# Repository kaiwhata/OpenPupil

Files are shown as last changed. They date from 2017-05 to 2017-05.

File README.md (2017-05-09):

# OpenPupil
Instuctions for assembly and/or fabrication of our open-source pupilometer.

# Overall system architecture
The overall system design can be seen in our poster presented at ARVO 2017 (https://www.arvo.org/AM/) here.
Our OpenPupil electronic system consists of: a Raspberry Pi 2 B+, with a NoIR camera, two 850nm IR LEDs, a 16 neopixel ring, USB wireless dongle, microSD card . 
Our hardware system consists of: a 3D printed eyepiece, a lazercut enclosure, a Google Cardboard lens
Our software system consists of: a python flask server, a supervisor instance, a C library and program for image collection and processing
A tabulated series of the above components is available below along with prices and purchasing suggestions.
For setup you will also (unless you're proficient with SSH and command line) need an HDMI cable, usb keyboard and mouse.

# Hardware instructions
You can find the lazercut enclosure designs (for 6mm acrylic) here.
You can find the `.stl` file for the 3D printed eyepiece here. Alternatively, if you do not have access to a 3D printer, you can purchase a printed one directly from our Shapeways store here (www.shapeways.com/shops/openpupil).

# RPi Installation instructions
`sudo apt-get install supervisor python-picamera`
`sudo pip install flask`

# Components

| Component     | Cost (USD)         | Purchasing Link |
| ------------- |:-------------:| -----:|
| RPi v2 B+ | $29.95 | https://www.adafruit.com/product/1914 | (a full kit can be purchased here: https://www.adafruit.com/product/2380)
| No IR camera | $29.95 | https://www.adafruit.com/product/387 |
| 850nm IR LEDs * | $0.75ea | https://www.adafruit.com/product/387 |
| Neopixel Ring | $9.95 | https://www.adafruit.com/product/1463 |
| USB Wifi Dongle | $11.95 | https://www.adafruit.com/product/814 |
| microSD card (8 or 16GB)| $14.95 | https://www.adafruit.com/product/1583 |
| 3D printed eyepiece | $ | |
| Google Cardboard v1 lens | $ | |

# Contact Details
This project is currently lead by Dr. Jesse Gale (jesse.gale@gmail.com) with support from Elf Eldridge (kaiwhata@gmail.com) and honours student Shaetrun Pathmanathan.

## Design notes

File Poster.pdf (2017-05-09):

Figure 1 Exploded view of device

# Hardware

# Proposal

# Methods

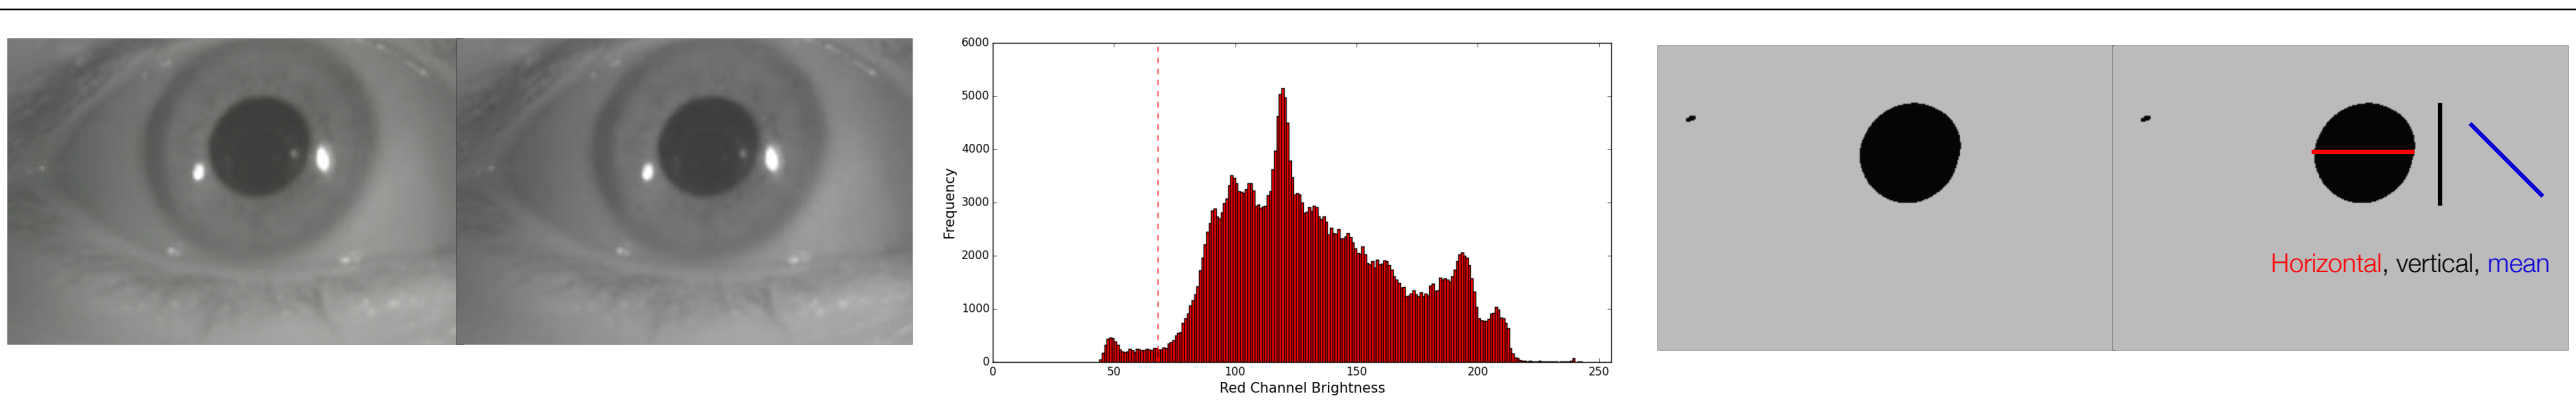
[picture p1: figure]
Horizontal, vertical, mean

## Contacts

To inquire or contribute, or to obtain one of these devices for your own research, please contact us.
Jesse Gale
jesse.gale@gmail.com
+64 21 1272 979
Surgery & Anaesthesia
University of Otago
PO Box 7343
Newtown
Wellington 6242
New Zealand

# Development of an open source pupilometer for testing melanopsin responses

# Dr Jesse Gale¹,2

# , Dr J. Elf Eldridge³

# , Shaetrun Pathmanathan³

# , Kapeteni Polutea³

# , Dr Gideon Gouws³, Prof Simon Fraser⁴

1) Surgery & Anaesthesia, University of Otago, Wellington, New Zealand. 2) Ophthalmology, Capital and Coast District Health Board, Wellington, New Zealand.
3) Engineering and Computer Science, Victoria University, Wellington, New Zealand. 4) Design, Victoria University, Wellington, New Zealand.

We identified the core requirements for versatile pupil testing in a wide range of scenarios, such as anisocoria, refractive surgery planning, testing pupils after head injury, quantifying a relative afferent pupil defect (RAPD), and potentially testing quadrants individually (what could be termed multifocal pupilometry).

These requirements were:
- A close fitting goggle to eliminate ambient light and provide illumination from a large visual angle
- An IR video camera with sufficient optical quality to allow filming of the pupil at high spatial and temporal resolution in both light and dark conditions
- Illumination of high intensity, fine control, all colours, and potentially directional illumination (e.g. testing sectors of the visual field)
- Portability, connecting to a computer or smartphone wirelessly, with a degree of internal data processing

We investigated the cheapest, widely-available components that would meet these requirements.

The design, software, and all early findings were made freely available on an open source directory in the spirit of collaboration.

https://github.com/kaiwhata/openpupil

# Software

Poster # 5090 – B0700

The intrinsically-photosensitive melanopsin-expressing retinal ganglion cells are of interest for several reasons. Quantifying melanopsin function with the post-illumination pupil response (PIPR) is of potential use in clinical research.

Moreover, a cheap and versatile pupilometer may have application in a range of research settings, neurological and ophthalmology practice, and in many primary care settings such as ambulances, emergency departments and family practice.

Standard video pupilometry uses infrared (IR) video of the pupil, lights to stimulate pupil constriction, and software to measure pupil size from the video. The PIPR additionally requires stimulating blue light of high luminance (> 100 mcdm⁻²). Portable pupilometers cost thousands of dollars and do not have capability to test PIPR, while PIPR is usually tested with non-portable electrophysiology equipment costing many tens of thousands of dollars.

Session Number: 489 – Pupil – May 10, 2017

## Can an affordable pupilometer be created using widely available technology, with the required capabilities to test melanopsin function as well as common clinical scenarios?

# Background

The proliferation of cheap components, powerful and versatile microprocessors,

## and 3D printers enables the development of

new clinical and research tools at low cost.

# Conclusions

Optics This biconvex lens functions to bring the camera into focus at a short working distance. These 25 mm plastic lenses of 22 D power are widely available for Google Cardboard virtual reality sets, at a cost < USD $0.40.

Goggle (housing) This functions to exclude ambient light, position the camera at the correct distance in front of the eye, and diffuse incident light to illuminate the whole field. It must be comfortable, ergonomic (fitting most orbits), and hygienic (easy to clean).

We have tested a range of designs and 3D printing materials. Further prototyping continues with flexible, cleanable materials that can diffuse light. Our intention is to provide all designs for free at 3D printing service and marketplace shapeways.com, allowing interested users to create the parts easily in the ideal materials at cost (approximately USD $10.00).

www.shapeways.com/shops/openpupil

Video camera This Raspberry Pi PiNoIR v2 video camera Is available for USD ~$25.00.

It has an 8 megapixel sensor and detects infrared (IR). We placed a photographic high pass IR filter over the camera and were able to exclude visible light while seeing the pupil in crisp detail. The camera has auto-focus and auto-exposure firmware that may be disabled. Frame rate is usually 25 Hz.

Micro-processor This Raspberry Pi 2 model B+ board is available for USD ~$38.00. It contains a
900 MHz quad-core central processing unit (CPU) with 1
GB random access memory (RAM), multiple ports and
interfaces. We intend to use the Raspberry Pi 3 with wireless interface and Bluetooth in upcoming prototypes.

Although other more powerful micro-computers are available, this is the cheapest board with the necessary specifications for image processing, data transfer and video display simultaneously. Software was written for the operation of the hardware and analysis of the collected video images using C++ programming on the Raspbian open source operating system.

## Total hardware costs – some assembly required

The plans to replicate this device are available open source for free access
and collaborative refinement. The components cost a total of approximately USD $140.00 plus a minor degree of circuit board connection and assembly with soldering and BluTack and a container. We hope that this hardware gains increasing use in research projects internationally.

Power source This battery pack is rechargeable with a simple USB cable and provides two power sources of 5 V, one 1 A supply for the stimulation LEDs and one 2 A supply for the Raspberry Pi and downstream devices. Batteries of this type are available with 10,000 mAh storage for USD $39.95

Stimulation This ring of 16 NeoPixel individually controllable
red, green and blue LEDs is widely
available for USD $10.00.

Each NeoPixel in the ring can control red, green and blue light individually with 255 levels of brightness. The maximal luminance of blue light is adequate to generate a robust PIPR. The ring arrangement allows for sectoral testing of the visual field.

Figure 2 Commercial images of 16 NeoPixel ring showing size, function

LED Colour | Wavelength (nm) | Luminous intensity (mcd)
Red | 620-630 | 550-700
Green | 515-530 | 1100-1400
Blue | 465-475 | 200-400

Figure 3 Images of the stimulation LEDs in use

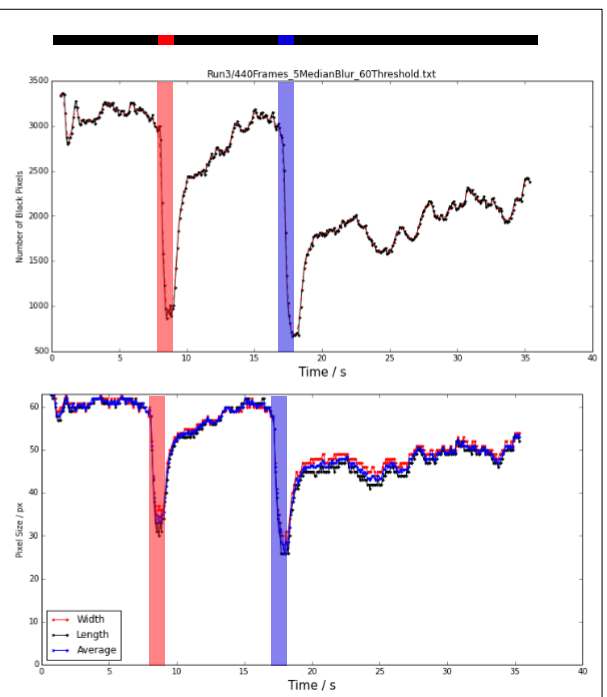
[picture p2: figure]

Figure 6 shows the pupil area above and pupil diameter below in response to 9 s darkness, then a bright red flash of 1 s, then 9 s darkness, then a bright blue flash of 1 s followed by darkness for 18
s. The PIPR to blue light is shown.

# Future directions

- Evaluation and refinement of the goggle design to improve ergonomics and hygiene
- Calibration of pupil size measures for accuracy and stimulation LED photometry for safety
- Validation studies comparing to existing pupilometry devices
- Development of phone application to enhance the portability and usability of the device
- Development of cloud based data storage and analysis

Background illumination Two super-bright 5 mm IR (940 nm) light emitting diodes (LEDs, cost USD $0.75 each) were housed in the goggle, providing background IR illumination of the pupil.

The program illustrated in figure 4 was used to record from volunteers in the laboratory, and a robust PIPR could be demonstrated (Figure 6). Processing time (using the RPi 2B+) board allows for real time measurement and display of pupil size at around 20 Hz, although raw video at a faster frame rate could be also be streamed for measurement in retrospect.

Experimentation with increasing contrast was found to reduce signal-to-noise ratio, median blur reduced single-pixel noise but slowed performance excessively, and the Canny edge-finding and Hough circle-finding algorithms resulted in errors and increased noise from reflections on the cornea (Figure 5).

Seed grant application
In process

Frame-by-frame image processing software was written using C++ language to run on the Raspbian operating system. The red channel was isolated, and histograms showed a peak of darkest pixels representing the pupil (Figure 4). Trial of numerous dynamic and static and adjusted threshold settings led to a static threshold at the luminance of the 6000th darkest pupil (after 10 s dark adaptation) to estimate the pupil signal. This led to a binary image for all subsequent video frames, from which pupil area (pixels), and vertical and horizontal and mean pupil diameter were calculated.

Unprocessed RGB | Red channel | Histogram, threshold shown | Binary image | Pupil diameter
Figure 4 showing the sequential processing of one frame by one iteration of the program.

## References

Funding was received from Capital Vision Research Trust

Kankipati L, et al. Post-illumination pupil response in subjects without ocular disease. IOVS 2010;2764 Kankipati L, et al. The post-illumination pupil response is reduced in glaucoma patients. IOVS 2011;52:2287 Kim T-H & Youn J-I. Development of a smartphone-based pupillometer. J Optic Soc Korea 2013;17:249 Kardon R, et al. Chromatic pupil responses. Ophthalmology 2009;116:1564
A full list of references, our production files and current
program codes, available at:

https://github.com/kaiwhata/openpupil

Increased contrast | Median blur | Hough algorithm
Figure 5 shows discarded processing techniques

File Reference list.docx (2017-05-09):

# Reference list

Wakakura M, Yokoe J Evidence for preserved direct pupillary light response in Leber’s hereditary optic neuropathy. BJO 1995;79(5):442–446.

Provencio I, et al. Melanopsin: An opsin in melanophores, brain, and eye. PNAS 1998;95:340–345

Bremner FD, et al. Comparing pupil function with visual function in patients with Leber’s hereditary optic neuropathy. IOVS 1999;40:2528-2534.

Provencio I., et al. A Novel Human Opsin in the Inner Retina. J Neurosci 2000;20:600

Bremner FD, et al. The pupil in dominant optic atrophy. IOVS, 2001:42(3):675–678.

Hattar S, et al. Melanopsin-containing retinal ganglion cells: architecture, projections, and intrinsic photosensitivity. Science 2002;295:1065–1070

Lucas RJ, et al. Diminished pupillary light reflex at high irradiances in melanopsin-knockout mice. Science 2003;299:245

Bose S et al. Relative post-mortem sparing of afferent pupil fibers in a patient with 3460 Leber’s hereditary optic neuropathy. Graefes Arch Clin Exp Ophthalmol 2005:243(11):1175–1179

Hattar S, et al. Central projections of melanopsin-expressing retinal ganglion cells in the mouse. J Comp Neurol 2006;497:326-349

Gamlin PDR, et al. Human and macaque pupil responses driven by melanopsin-containing retinal ganglion cells Vision Res 2007;47:946-954

Kalaboukhova I, Fridhammar V, Lindblom B. Relative afferent pupillary defect in glaucoma: a pupillometric study. Acta Ophthalmol Scand 2007;85:519-525.

Güler AD, et al. Melanopsin cells are the principal conduits for rod–cone input to non-image-forming vision. Nature 2008;453:102-106.

Mure, L.S. et al. Melanopsin bistability: a fly’s eye technology in the human retina. PLoS ONE 2009;4:e5991

Kardon R, et al. Chromatic pupil responses: Preferential activation of the melanopsin-mediated versus outer photoreceptor-mediated pupil light reflex. Ophthalmology 2009;116:1564–1573

Roecklein, K.A. et al. A missense variant (P10L) of the melanopsin (OPN4) gene in seasonal affective disorder. J. Affect. Disord. 2009;114:279–285

Ecker JL, et al. Melanopsin-expressing retinal ganglion-cell photoreceptors: cellular diversity and role in pattern vision. Neuron 2010;67:49–60

Brown TM, Gias C, Hatori M, Keding SR, Semo M, Coffey PJ, Gigg J, Piggins HD, Panda S, Lucas RJ. Melanopsin contributions to irradiance coding in the thalamo-cortical visual system. PLoS Biol 2010;8:e1000558

Allen AE, et al. Visual responses in mice lacking critical components of all known retinal phototransduction cascades. PLoS ONE 2010;5:e15063.

Kawasaki, A., Herbst, K., Sander, B., & Milea, D. (2010). Selective wavelength pupillometry in Leber hereditary optic neuropathy. Clinical and Experimental Ophthalmology, 38(3), 322–324.

La Morgia et al. 2010 Melanopsin retinal ganglion cells are resistant to neurodegeneration in mitochondrial optic neuropathies. Brain 2010: 133; 2426–2438

Kankipati L, et al. Post-illumination pupil response in subjects without ocular disease. IOVS 2010;51:2764–2769

Chen S-K, Badea TC, Hattar S. Photoentrainment and pupillary light reflex are

mediated by distinct populations of ipRGCs. Nature 2011;92:476

La Morgia C (http://www.ncbi.nlm.nih.gov/pubmed?term=La%20Morgia%20C%5BAuthor%5D&cauthor=true&cauthor_uid=20691201), Ross-Cisneros FN (http://www.ncbi.nlm.nih.gov/pubmed?term=Ross-Cisneros%20FN%5BAuthor%5D&cauthor=true&cauthor_uid=20691201), Hannibal J (http://www.ncbi.nlm.nih.gov/pubmed?term=Hannibal%20J%5BAuthor%5D&cauthor=true&cauthor_uid=20691201), Montagna P (http://www.ncbi.nlm.nih.gov/pubmed?term=Montagna%20P%5BAuthor%5D&cauthor=true&cauthor_uid=20691201), Sadun AA (http://www.ncbi.nlm.nih.gov/pubmed?term=Sadun%20AA%5BAuthor%5D&cauthor=true&cauthor_uid=20691201), Carelli V (http://www.ncbi.nlm.nih.gov/pubmed?term=Carelli%20V%5BAuthor%5D&cauthor=true&cauthor_uid=20691201). Melanopsin-expressing retinal ganglion cells: implications for human diseases. Vision Res. 2011;51(2):296-302.

Kankipati L, et al. The post-illumination pupil response is reduced in glaucoma patients. IOVS 2011;52:2287–2292

Feigl B, et al. Intrinsically photosensitive (melanopsin) retinal ganglion cell function in glaucoma. IOVS 2011;52:4362–4367

Moura ALA, et al. The pupil light reflex in Leber’s hereditary optic neuropathy: Evidence for preservation of melanopsin-expressing retinal ganglion cells. IOVS 2013;54:4471–4477
